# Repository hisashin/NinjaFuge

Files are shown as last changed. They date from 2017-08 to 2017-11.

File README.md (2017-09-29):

NinjaFuge
==========

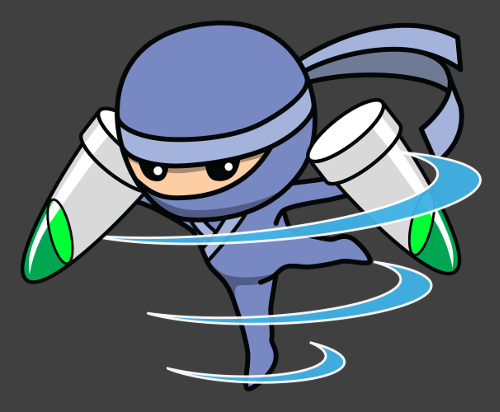
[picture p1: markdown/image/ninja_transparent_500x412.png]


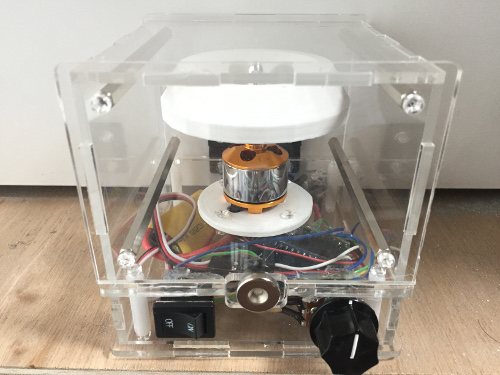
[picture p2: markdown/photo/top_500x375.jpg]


Youtube (http://www.youtube.com/watch?v=6wPBDhJhW8Q)

Opensource ([CC BY-NC-SA 2.5](https://creativecommons.org/licenses/by-nc-sa/2.5/)) centrifuge with cover sensor and lock. Derived from [F.Lab's one](http://www.instructables.com/id/3D-Printed-DIYbio-Mini-Centrifuge/).

- [Frequently asked questions](#faq)
- [Changelog](#change)
- [Please note before making](#note)
- [Bill of material](#bom)
- [Wirings](#wire)
- [Source code](https://github.com/hisashin/NinjaFuge/blob/master/sourcecode/NinjaFuge/NinjaFuge.ino)
- [Assembly instructions](#assembly)

### FAQ

- How much?

	I made at $20 from junks. If you buy everythings new in Japan, total parts price is $75 now.

- How fast?

	Max 12,000RPM in my case by connecting 12V adapter to cheapest ($10) 1000KV (that means +1000RPM per 1V) motor. You can make it faster if you use higher voltage, faster motor or enough ampere. Do not exceed absolute maximum voltages of motor, ESC and microcontroller.

### Changelog

- 2017 Aug 7 : Changes from [F.Lab's one](http://www.instructables.com/id/3D-Printed-DIYbio-Mini-Centrifuge/)
	- Enclosure is changed from 3d printing to acrylic lasercut. because I think printing takes too long time and easier to get fail.
	- Added magnet to cover and reed switch to base. so that it can stop rorating when cover is opened.
- 2017 Aug 8 : Add safety lock
	- I don't know how to brake motor and it takes seconds to stop rorating. That means it's still not safe perfectly. 
	Small servo motor should be added to lock the cover while rotating.

### Notes before making

- Any hinge around you can be used but yours will not be same as mine. Don't forget to change holes on both cover_back and base_back to yours.
- Similar minor changes will be required for other parts like motor, variable resistor and switch. If you use bigger Arduino, basement should be wider.
- I used acrylic board, polycarbonate screws and nuts. If you want to proof it against rotor break, polycarbonate board, steel screws and [nylon nuts](https://en.wikipedia.org/wiki/Nyloc_nut) are recommended.

### Bill of material

- Lasercut 3mm acrylic or polycarbonate parts with [this](https://github.com/hisashin/NinjaFuge/blob/master/lasercut/NinjaFuge_3mm_clear.pdf).
- 3d printed [rotor](https://github.com/hisashin/NinjaFuge/blob/master/3dprint/stl/NinjaFuge_F.lab_Rotor.stl) and [motor base](https://github.com/hisashin/NinjaFuge/blob/master/3dprint/stl/NinjaFuge_motor_holder.stl) with any material.
- Some heat shrinkable tubes with different diameters are useful to protect solderings.
- Small microcontroller like [Arduino Nano](https://store.arduino.cc/usa/arduino-nano) ($22), [Arduino Pro Mini](http://www.sparkfun.com/products/11113) ($10) or anything you like. If you can make Arduino with [Arduino](https://www.arduino.cc/en/Tutorial/ArduinoISP) or [AVRISP mkII](http://www.atmel.com/tools/avrispmkii.aspx), single [ATmega328](https://www.digikey.jp/product-detail/ja/microchip-technology/ATMEGA328P-PU/ATMEGA328P-PU-ND/1914589) ($2.2) is enough. In any case, these pins are required.
	- 1 analog input for tune
	- 1 digital input to catch [interrupt](https://www.arduino.cc/en/Reference/AttachInterrupt) of reed switch
	- 2 digital output for ESC and door lock servo. VCC should be connected to them too. Refer [Wirings](#wire).
- Parts for enclosure
	- 29 M3 10mm screws
	- 8 M3 nuts
	- 4 M3 25mm spacer (both female) for base
	- 3 M3 100mm spacer (both female) for cover
	- To hold door lock servo, I used
		- 2 M2 8mm screws
		- 2 M2 nuts

- Are you living in Japan as me? Good. No need to change lasercut design if you use them.

	- [Brushless motor and ESC kit](https://www.amazon.co.jp/gp/product/B01MTCBO7D/ref=oh_aui_detailpage_o09_s00?ie=UTF8&psc=1)
	- [Small servo to lock door]()
	- [Variable resistor](http://akizukidenshi.com/catalog/g/gP-00246/)
	- [Nob for resistor](http://akizukidenshi.com/catalog/g/gP-00246/)
	- [Single circuit locker switch](https://www.sengoku.co.jp/mod/sgk_cart/detail.php?code=3A8K-4BFY)
	- [Neodymium magnet](http://www.sengoku.co.jp/mod/sgk_cart/detail.php?code=EEHD-4VZZ)
	- [Reed switch](http://akizukidenshi.com/catalog/g/gP-03676/)
	- [Hinge](https://hands.net/goods/4991807041906/)
	- [4 rubber foot if you want](http://www.sengoku.co.jp/mod/sgk_cart/detail.php?code=6AZE-JELC)
	- [DC jack](http://www.sengoku.co.jp/mod/sgk_cart/detail.php?code=EEHD-0HMZ)
	- [12V AC adapter](http://akizukidenshi.com/catalog/g/gM-06961/)
		- 5A looks well. 1A wasn't enough. If you need maximum RPM, check how much ampere your ESC needs.

- If not, it would be cheaper to find items similar to above list around you and move [holes](https://github.com/hisashin/NinjaFuge/blob/master/lasercut/NinjaFuge_3mm_clear.pdf) a little for each of them.

### Wirings

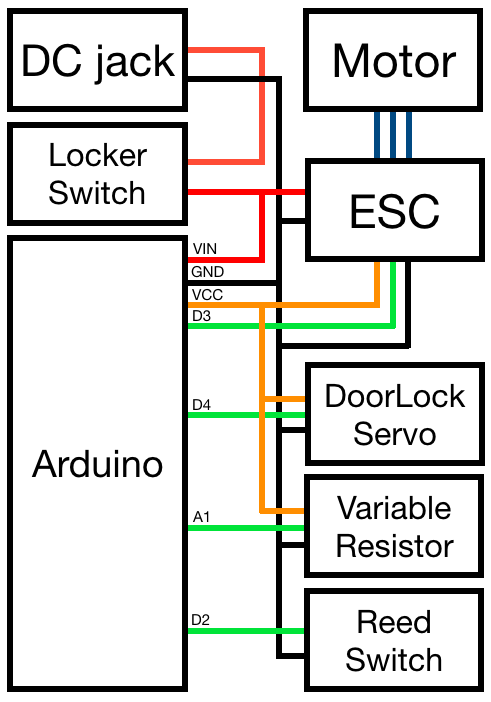
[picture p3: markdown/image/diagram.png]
diagram


### Assembly instructions

- Need to make latest model from scratch taking photos or movies to document here. Anyone want to do that?

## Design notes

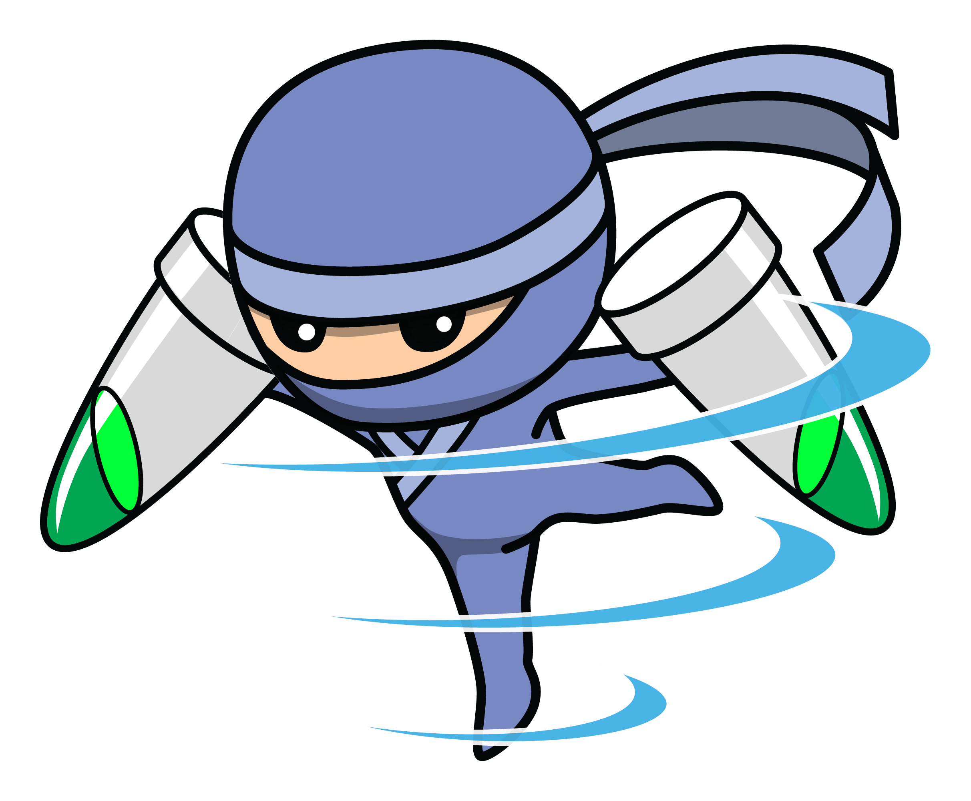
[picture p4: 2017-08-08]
markdown/image/ninja_transparent_2425x2000.png

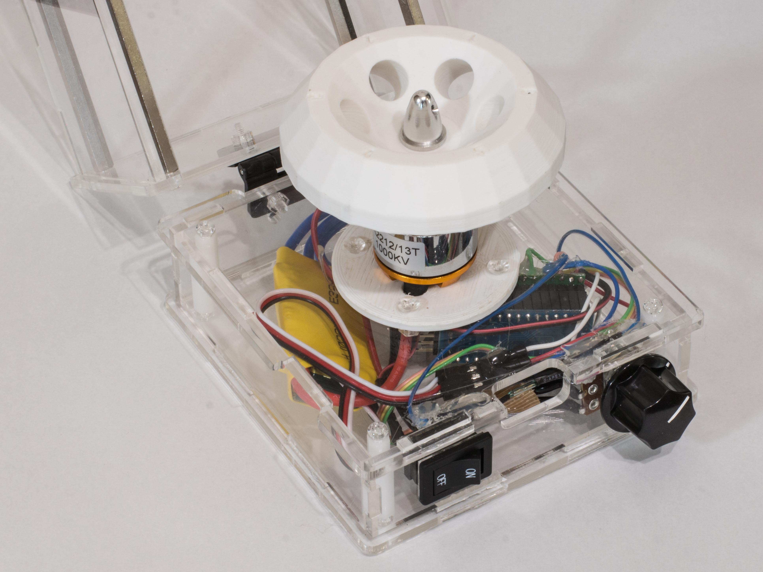
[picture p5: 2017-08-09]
markdown/photo/open5.jpg

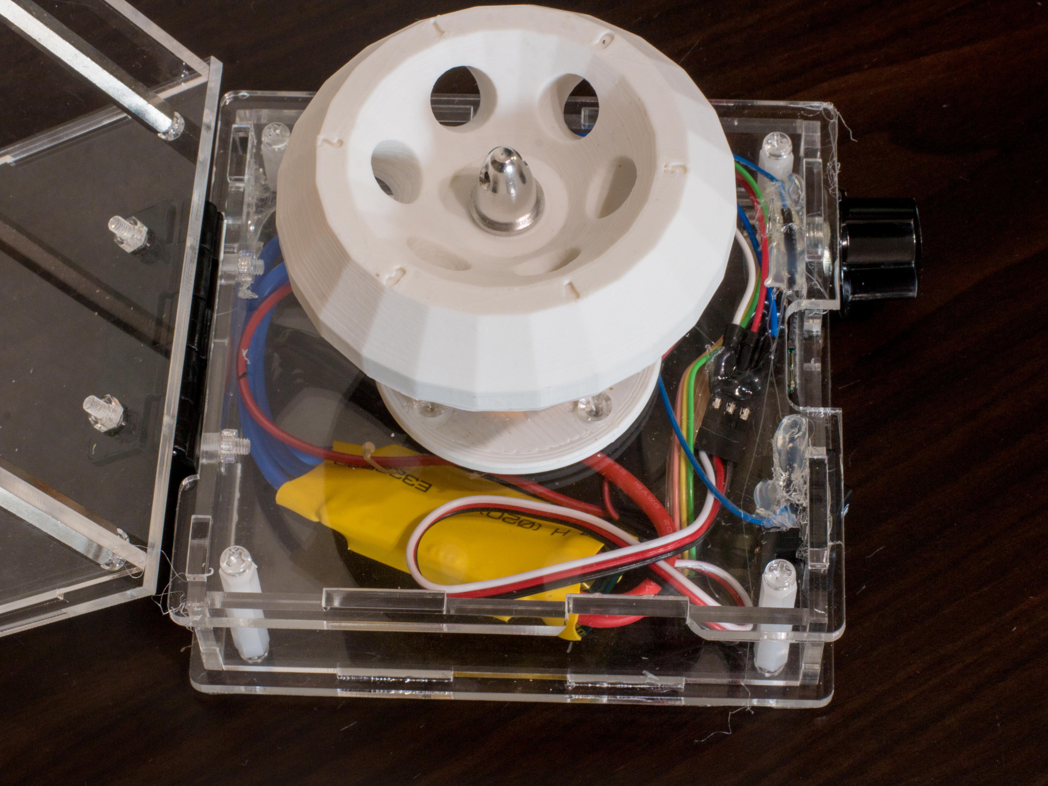
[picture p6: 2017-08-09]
markdown/photo/open4.jpg

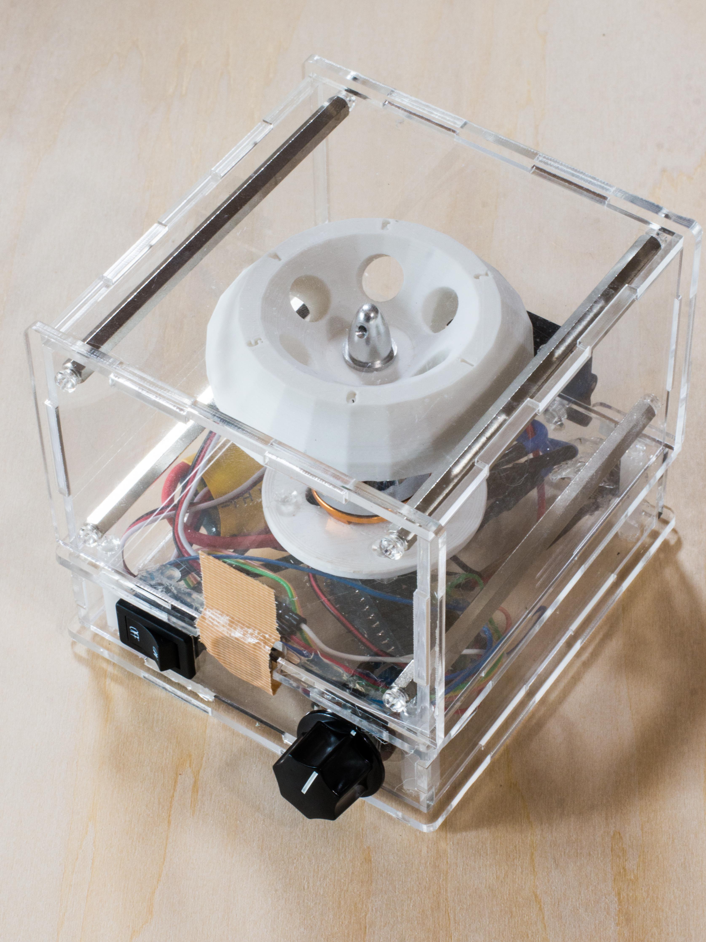
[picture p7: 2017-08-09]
markdown/photo/closed1.jpg

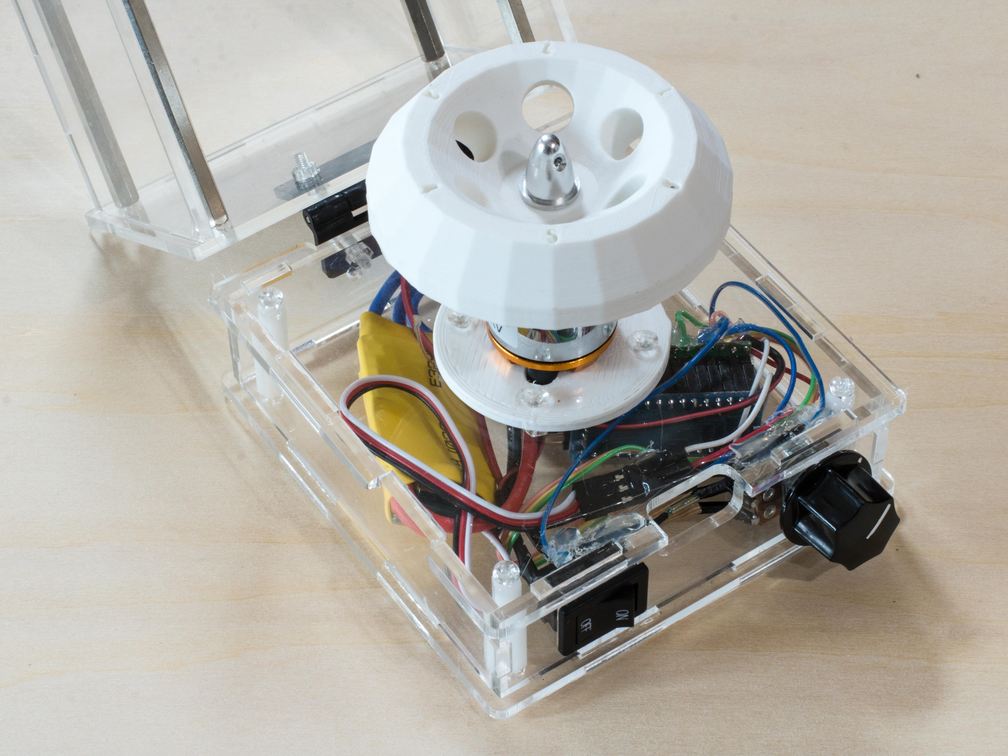
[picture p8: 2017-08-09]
markdown/photo/open8.jpg

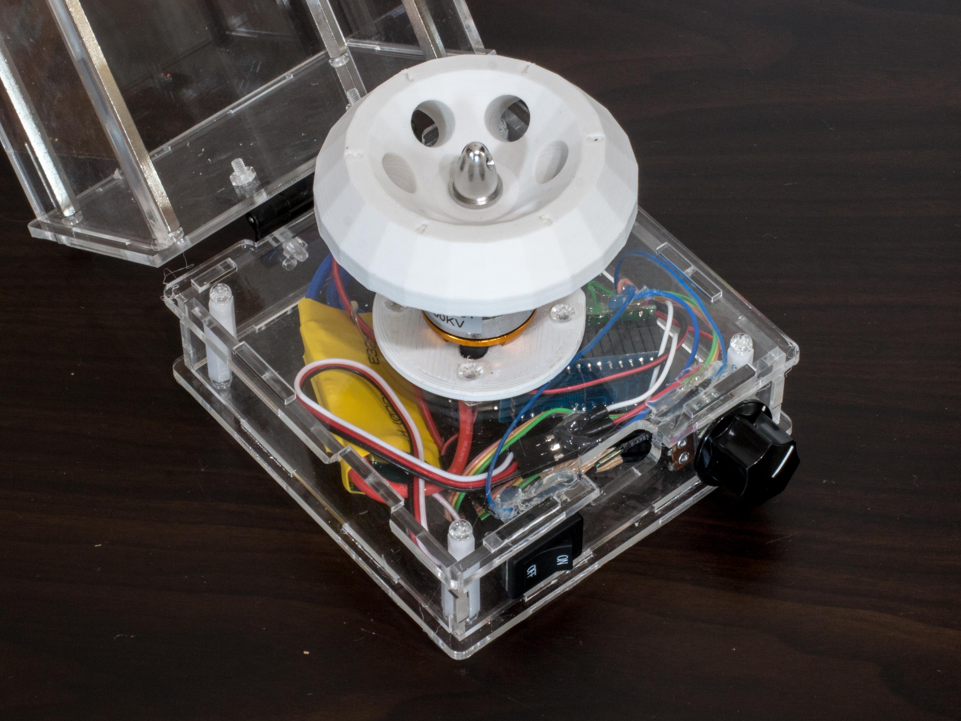
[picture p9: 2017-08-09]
markdown/photo/open1.jpg

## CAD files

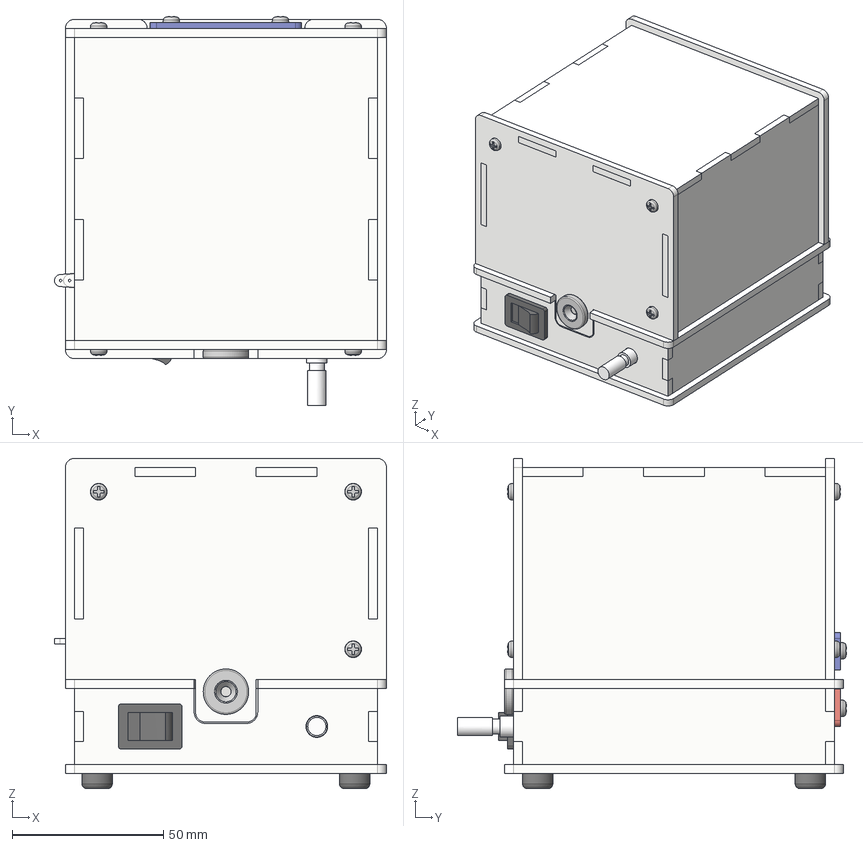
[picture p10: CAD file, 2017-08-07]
3dmodel/NinjaFuge.iges
109.6 x 128.5 x 109.0 mm

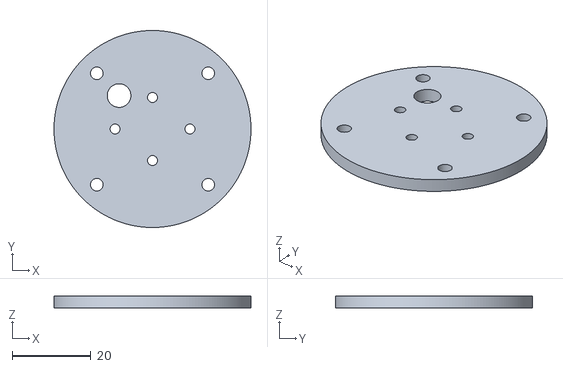
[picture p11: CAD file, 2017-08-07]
3dprint/stl/NinjaFuge_motor_holder.stl
50.0 x 50.0 x 3.00

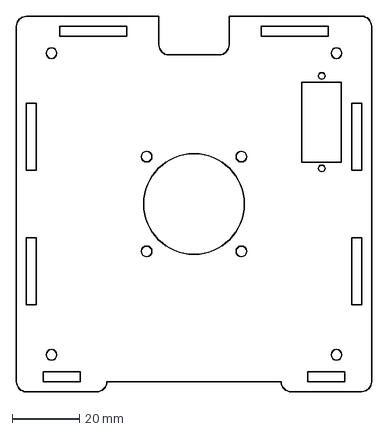
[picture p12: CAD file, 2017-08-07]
lasercut/dxf/3mm_clear_base_top.dxf
106.0 x 112.0 mm

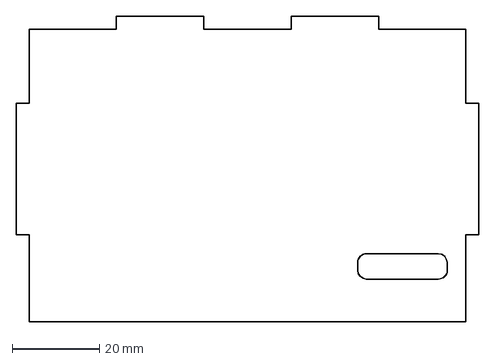
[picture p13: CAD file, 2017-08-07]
lasercut/dxf/3mm_clear_cover_left.dxf
106.0 x 70.0 mm

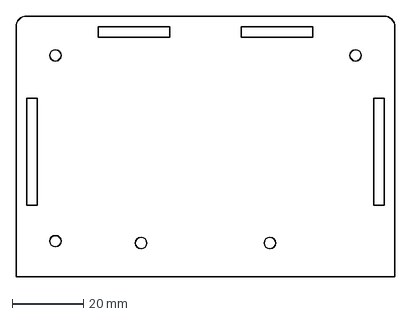
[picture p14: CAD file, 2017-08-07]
lasercut/dxf/3mm_clear_cover_back.dxf
106.0 x 73.0 mm

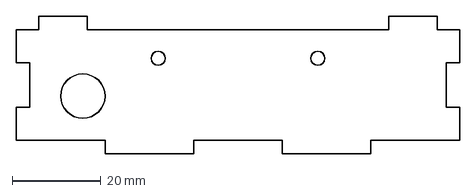
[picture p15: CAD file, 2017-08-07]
lasercut/dxf/3mm_clear_base_back.dxf
100.0 x 31.0 mm

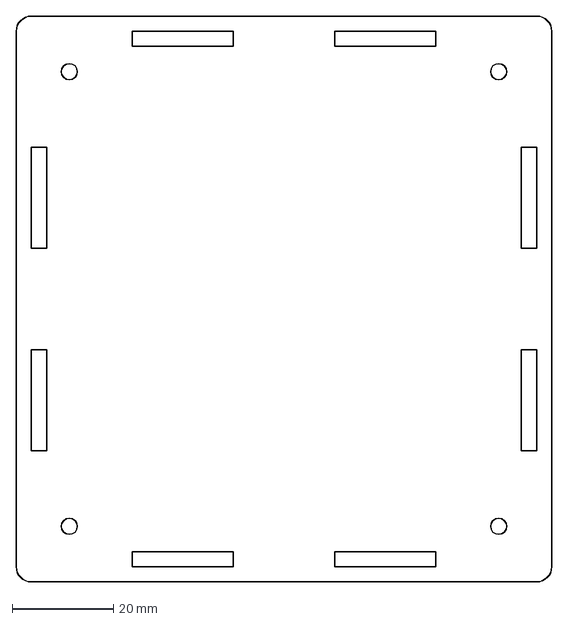
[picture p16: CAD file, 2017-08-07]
lasercut/dxf/3mm_clear_base_bottom.dxf
106.0 x 112.0 mm

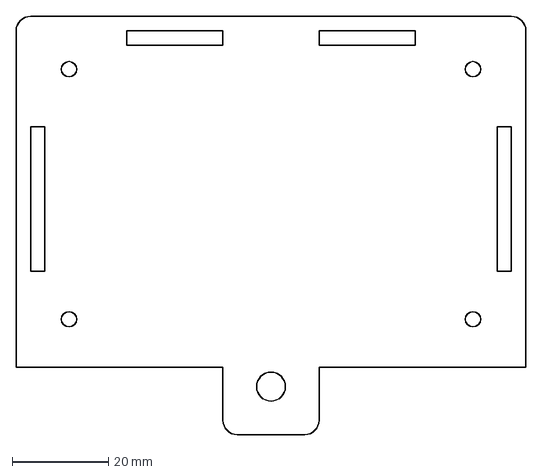
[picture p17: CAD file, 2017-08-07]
lasercut/dxf/3mm_clear_cover_front.dxf
106.0 x 87.0 mm

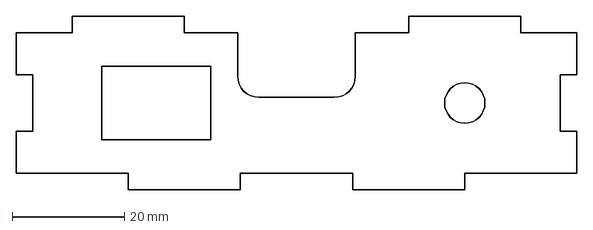
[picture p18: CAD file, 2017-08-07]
lasercut/dxf/3mm_clear_base_front.dxf
100.0 x 31.0 mm

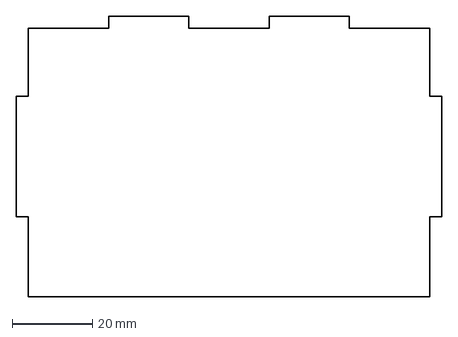
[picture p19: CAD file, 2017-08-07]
lasercut/dxf/3mm_clear_cover_right.dxf
106.0 x 70.0 mm

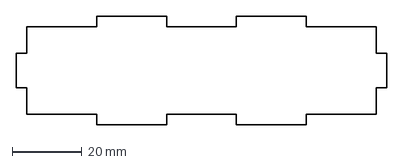
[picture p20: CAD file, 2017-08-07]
lasercut/dxf/3mm_clear_base_side_x2.dxf
106.0 x 31.0 mm

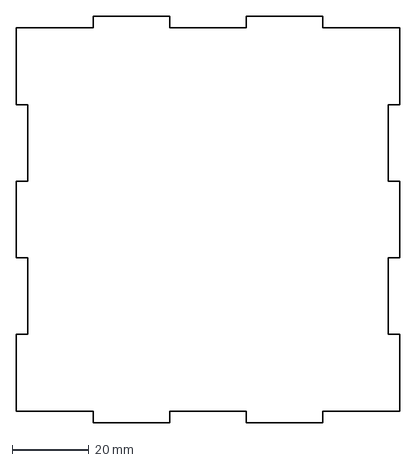
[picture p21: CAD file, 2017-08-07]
lasercut/dxf/3mm_clear_cover_top.dxf
100.0 x 106.0 mm

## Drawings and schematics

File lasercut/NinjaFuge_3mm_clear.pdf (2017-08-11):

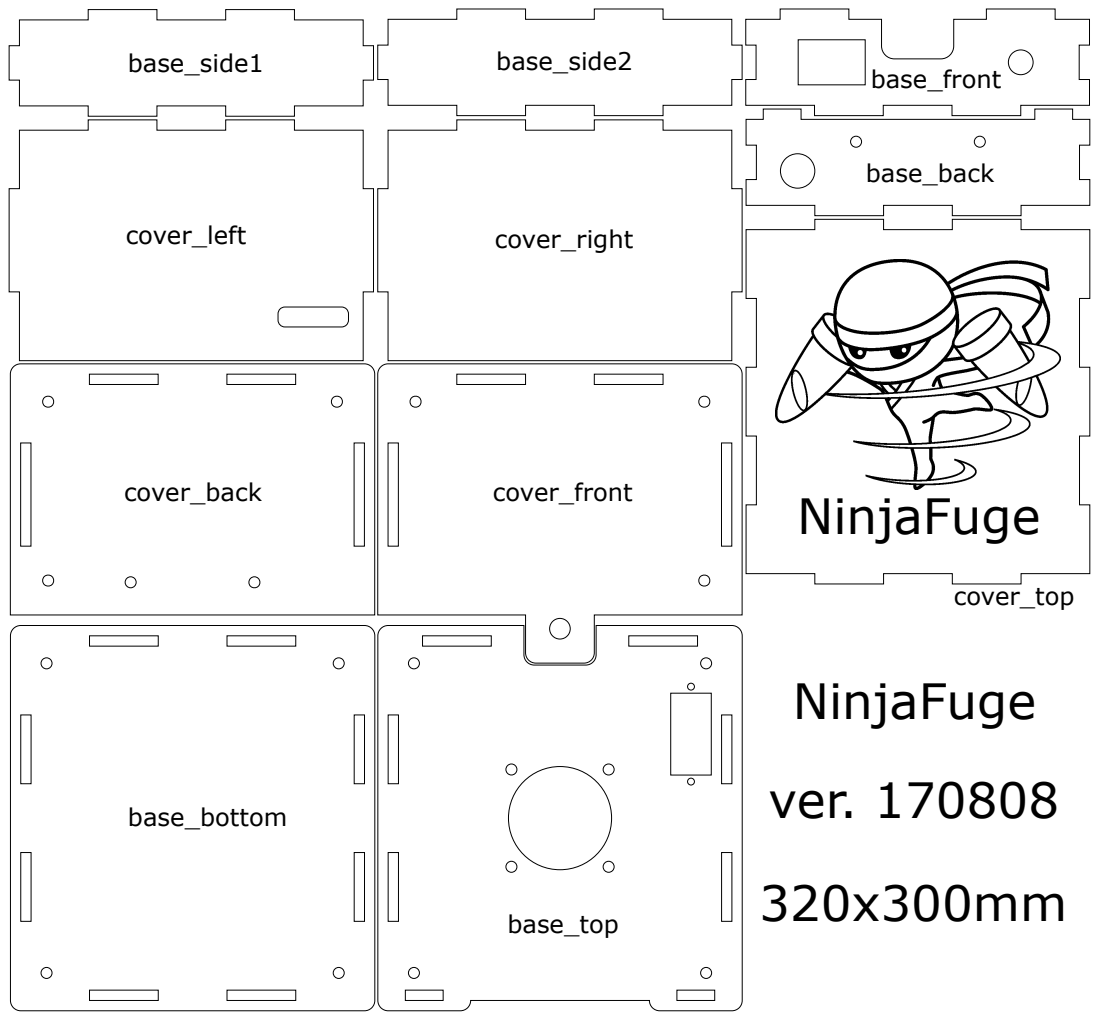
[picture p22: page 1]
base_side2; cover_left; base_side1; cover_right; cover_back; cover_front; base_bottom; base_top; cover_top; base_front; base_back; NinjaFuge; ver. 170808

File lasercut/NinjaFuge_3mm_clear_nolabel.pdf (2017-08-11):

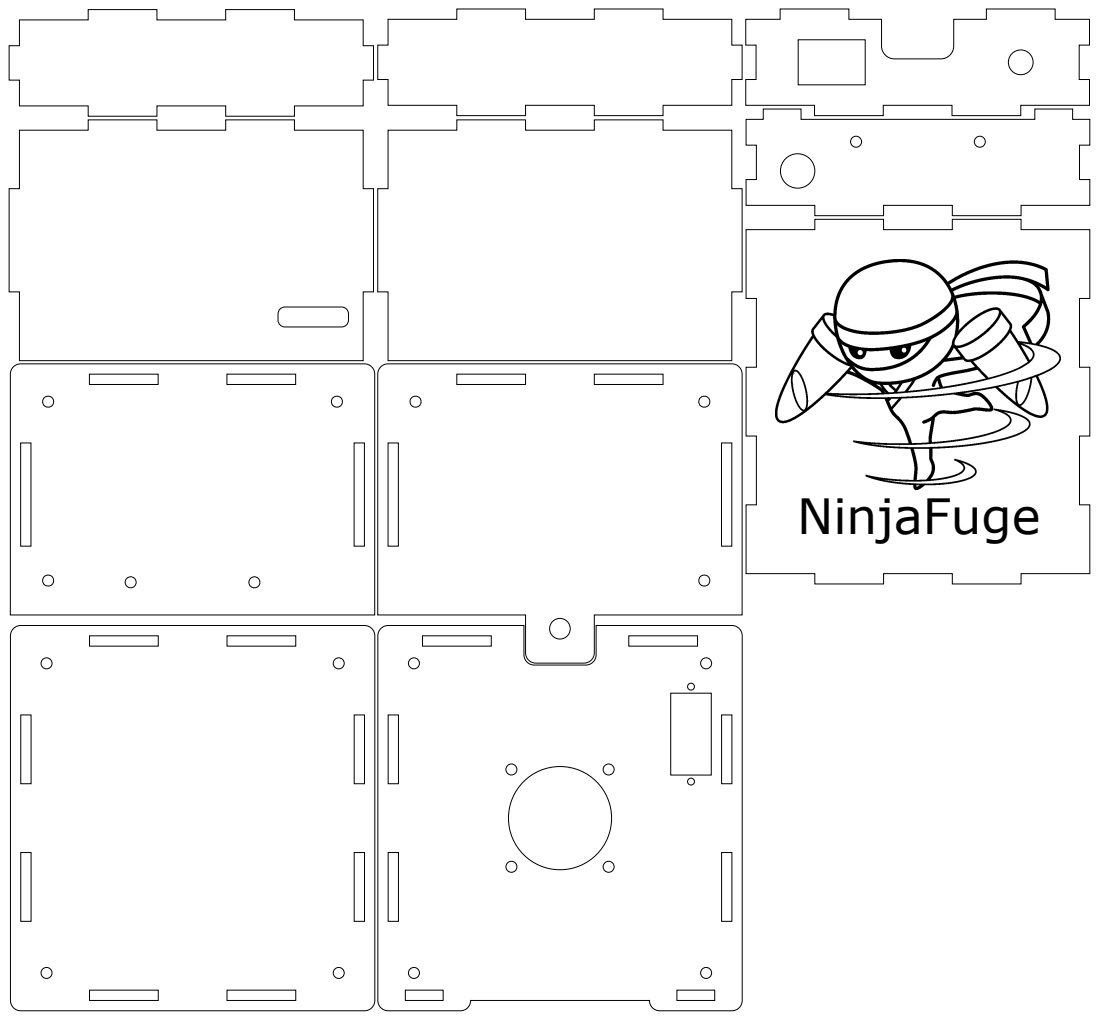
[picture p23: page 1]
NinjaFuge

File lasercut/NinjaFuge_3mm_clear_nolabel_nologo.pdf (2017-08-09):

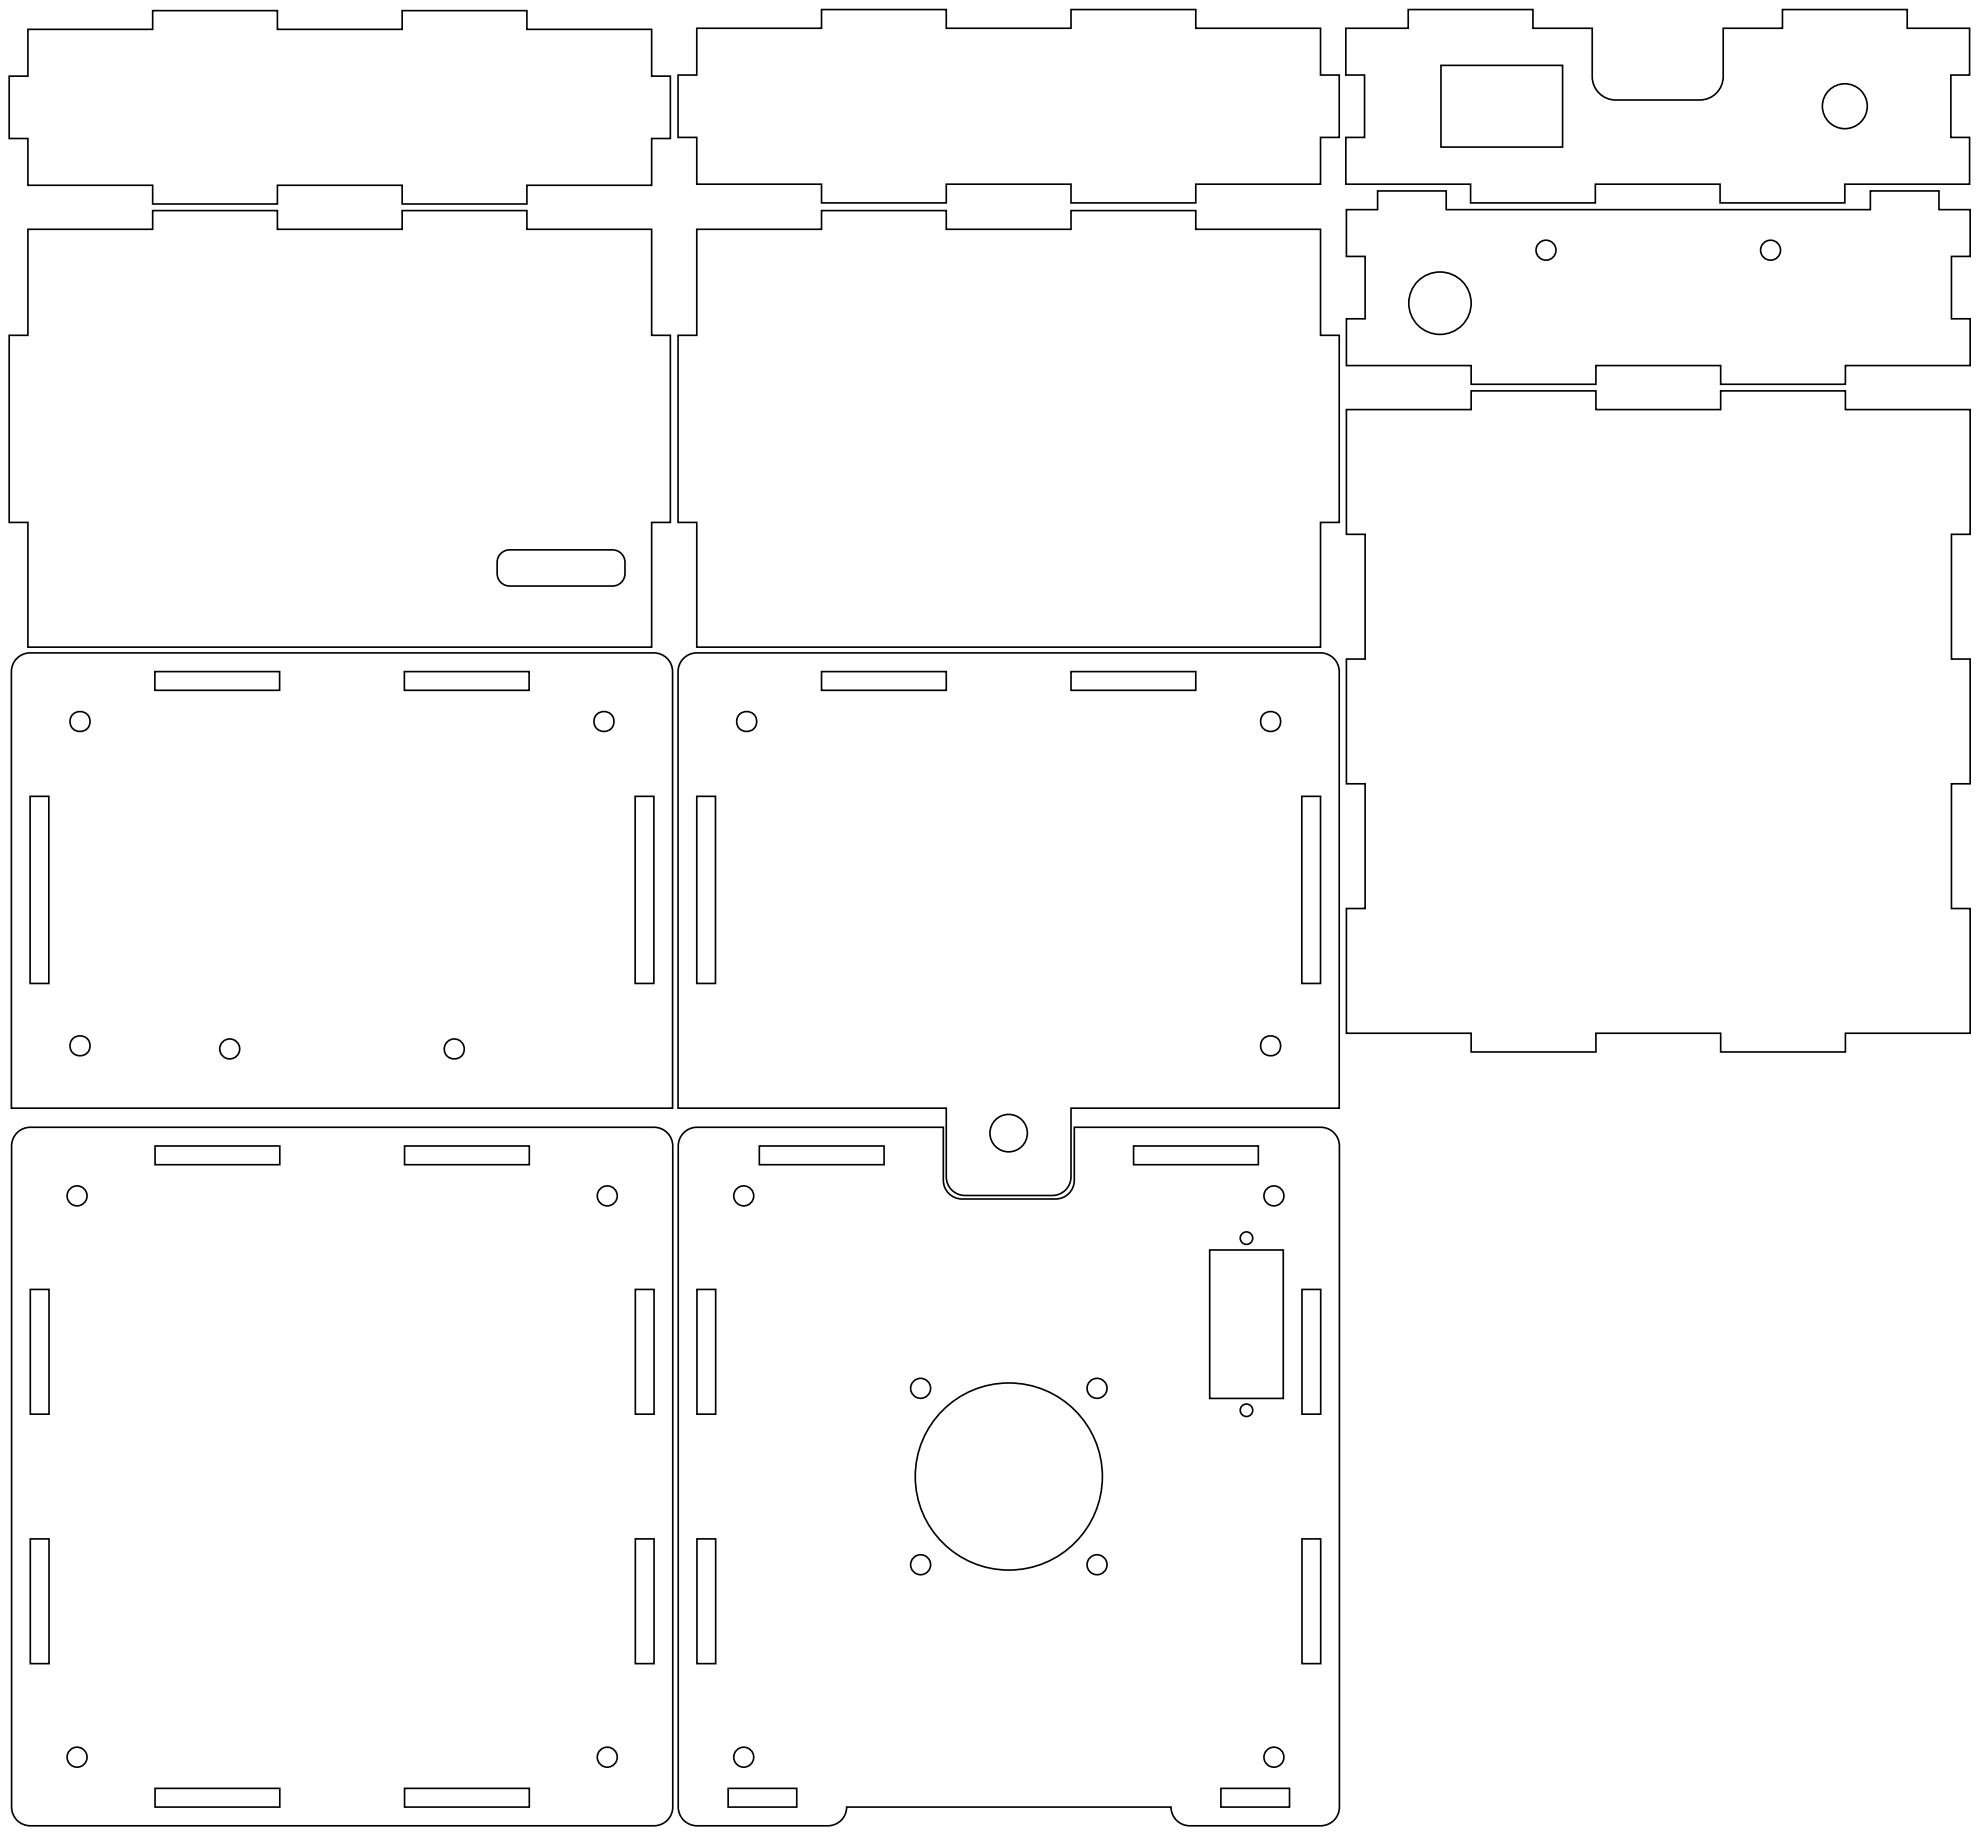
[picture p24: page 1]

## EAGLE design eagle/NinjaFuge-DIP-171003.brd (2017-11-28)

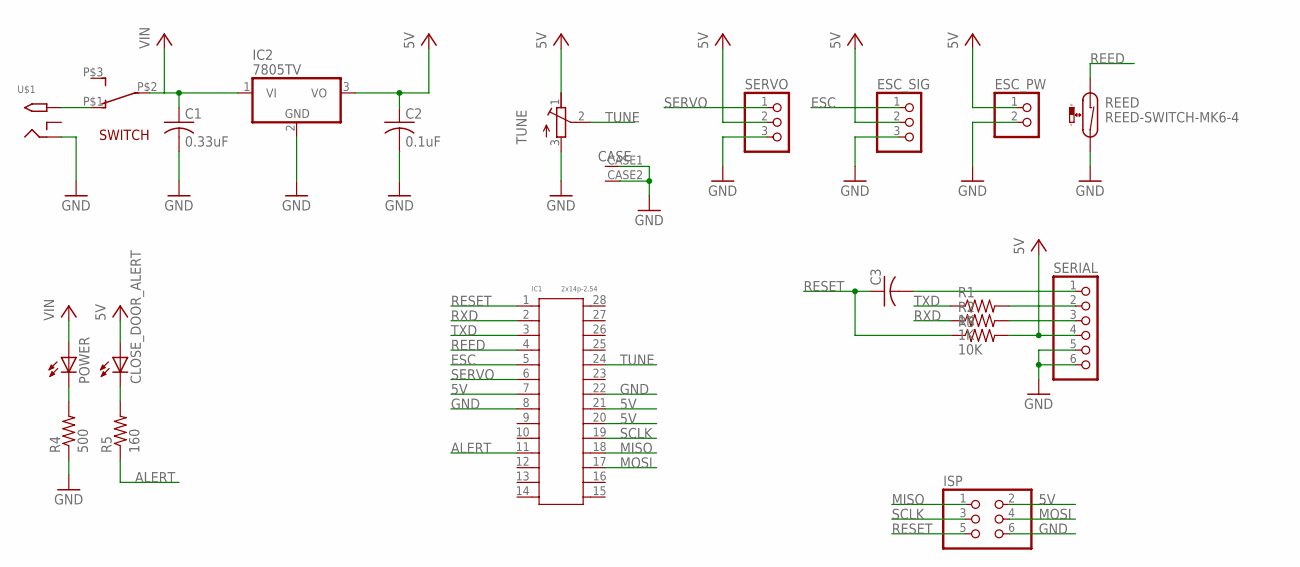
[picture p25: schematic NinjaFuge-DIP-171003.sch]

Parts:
C1: 0.33uF; C050-024X044
C2: 0.1uF; C050-024X044
C3: C-US050-024X044; C050-024X044
CLOSE_DOOR_ALERT: LED3MM
ESC_PW: PINHD-1X2; 1X02
ESC_SIG: PINHD-1X3; 1X03
IC1: 2x14p-2.54; SCK28-2.54-35.6X10MM
IC2: 7805TV; TO220V
ISP: PINHD-2X3; 2X03
POWER: LED3MM
R1, R2: 1K; 0204/5
R3: 10K; 0204/5
R4: 500; 0204/5
R5: 160; 0204/5
REED: REED-SWITCH-MK6-4; MK6-4
SERIAL: PINHD-1X6; 1X06
SERVO: PINHD-1X3; 1X03
SWITCH: MARUSHIN_MSR5
TUNE: RK09D117000B
U$1: 2.1MMJACKTHM; PJ-102A

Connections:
5V: C2.1, CLOSE_DOOR_ALERT.A, ESC_SIG.2, IC1.7, IC1.20, IC1.21, IC2.3 (VO), ISP.2, R3.2, SERIAL.4, SERVO.2, TUNE.1
ALERT: IC1.11, R5.1
ESC: ESC_SIG.1, IC1.5
GND: C1.2, C2.2, ESC_PW.2, ESC_SIG.3, IC1.8, IC1.22, IC2.2 (GND), ISP.6, R4.1, REED.2, SERIAL.5, SERIAL.6, SERVO.3, TUNE.3, TUNE.CASE1, TUNE.CASE2, U$1.RING
MISO: IC1.18, ISP.1
MOSI: IC1.17, ISP.4
unnamed: SWITCH.P$1 (1), U$1.TIP
unnamed: R2.2, SERIAL.3
unnamed: R1.2, SERIAL.2
unnamed: POWER.K (C), R4.2
unnamed: C3.2, SERIAL.1
unnamed: CLOSE_DOOR_ALERT.K (C), R5.2
REED: IC1.4, REED.1
RESET: C3.1, IC1.1, ISP.5, R3.1
RXD: IC1.2, R2.1
SCLK: IC1.19, ISP.3
SERVO: IC1.6, SERVO.1
TUNE: IC1.24, TUNE.2
TXD: IC1.3, R1.1
VIN: C1.1, ESC_PW.1, IC2.1 (VI), POWER.A, SWITCH.P$2 (2)

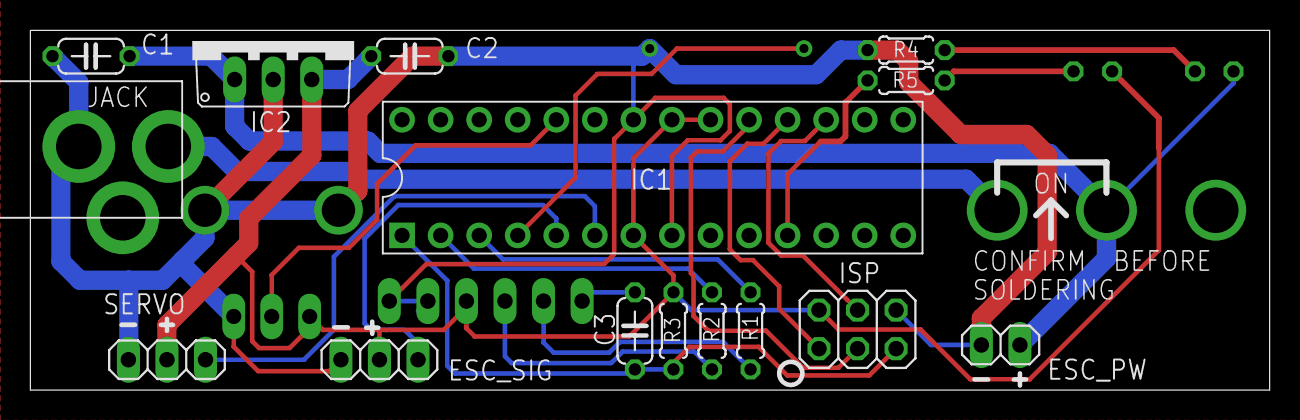
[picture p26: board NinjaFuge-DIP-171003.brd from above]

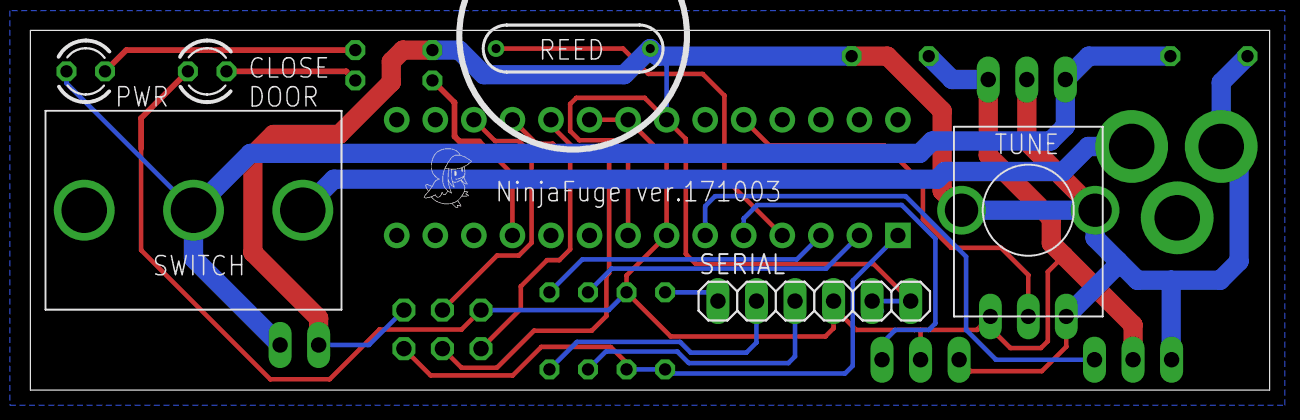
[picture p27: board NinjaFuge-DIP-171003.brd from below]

Board: 2 copper layers, 81.7 x 23.7 mm, 22 parts (7 on the bottom side), 20 nets.

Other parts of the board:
U$2: TORI_0.125

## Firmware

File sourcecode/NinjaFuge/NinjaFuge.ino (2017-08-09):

#include <Servo.h>

#define PIN_VR 0
#define PIN_MAGNET 2
#define PIN_ESC 3
#define PIN_LED 13
#define SPEED_STOP 500
#define SPEED_MIN 1150
#define SPEED_MAX 1500

Servo myservo;

boolean doorOpen;

void setup() { 
  pinMode(PIN_LED, OUTPUT);
  digitalWrite(PIN_LED, LOW);
  pinMode(PIN_MAGNET, INPUT_PULLUP);
  attachInterrupt(digitalPinToInterrupt(PIN_MAGNET), checkDoor, CHANGE);
  myservo.attach(PIN_ESC);
  calib();
  doorOpen = !isMagExists();
  Serial.begin(9600);
  if(doorOpen) {
    Serial.println("initial door=open" );
  } else {
    Serial.println("initial door=closed" );
  }
}

int val;

void loop() { 
  delay(400);
  if(doorOpen) {
    val = SPEED_STOP;
  } else {
    val = analogRead(PIN_VR);
    val = map(val, 1023, 0, SPEED_MIN, SPEED_MAX);
  }
  //Serial.println("val=" + val);
  myservo.writeMicroseconds(val);
}

boolean isMagExists() {
  return !digitalRead(PIN_MAGNET);
}

void checkDoor() {
  doorOpen = !isMagExists();
  if(doorOpen) {
    Serial.println("checkDoor door=open" );
  } else {
    Serial.println("checkDoor door=closed" );
  }
  digitalWrite(PIN_LED, !doorOpen);
}

void calib() {
  myservo.write(0);
  //myservo.writeMicroseconds(SPEED_MIN);
  delay(1000);
  myservo.write(30);
  //myservo.writeMicroseconds(SPEED_MAX);
  delay(3000);
}

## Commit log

2017-08-07 move dir
    [3mm_clear_base_back.dxf, 3mm_clear_base_bottom.dxf, 3mm_clear_base_front.dxf, 3mm_clear_base_side_x2.dxf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]
2017-08-07 door lock added
    [3mm_clear_base_back.dxf, 3mm_clear_base_top.dxf, 3mm_clear_cover_back.dxf, 3mm_clear_cover_left.dxf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]
2017-08-09 update lasercut
2017-09-29 fixing things
    [NinjaFuge-170925.sch]
2017-10-03 add pcb
    [NinjaFuge-DIP-171003.GBL, NinjaFuge-DIP-171003.GBO, NinjaFuge-DIP-171003.GBS, NinjaFuge-DIP-171003.GTL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]
2017-10-09 ordered pcb
    [NinjaFuge-DIP-171003.GBL, NinjaFuge-DIP-171003.GBO, NinjaFuge-DIP-171003.GBS, NinjaFuge-DIP-171003.GTL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]
2017-11-28 added another reed to check lock is locked or just hitting the wall
    [NinjaFuge-DIP-171003.brd, NinjaFuge-DIP-171128.brd, NinjaFuge-DIP-171128.sch]
